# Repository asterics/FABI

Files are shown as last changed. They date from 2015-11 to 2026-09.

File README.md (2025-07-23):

# Welcome to FABI

The FABI (Flexible Assistive Button Interface) allows control of a computer’s mouse cursor or
keyboard by just using momentary switches. This can be helpful for people who want to create 
user interactions with the press of a button - and it allows people who can't use standard computer input devices
to play games, surf the internet, communicate and much more.

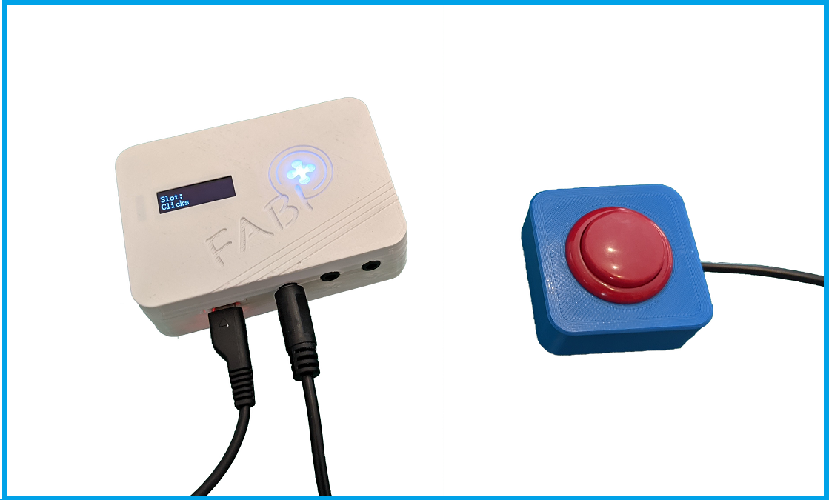
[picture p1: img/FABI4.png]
A FABI box with attached 3d-printed switch FABI box with attached switch


## How?

The FABI Interface can be actuated via dedicated buttons, momentary switches or self-made
electrical contacts. Additionally, a sip-puff sensor can be used to create user input.
FABI consists of a hardware module (a low-cost microcontroller which behaves
as a computer mouse and/or keyboard) and a config manager software for configuration of
the desired functions. The FABI system can be attached to computers, tablets or smart phones via USB.
Additionally, a bluetooth-module is available for devices that do not have a USB port (some Android or iOS phones).

## Folder structure of this repository
Essential information can be found in the following folders
* _Case Designs:_ different 3d-printable / lasercut designs for enclosures
* _Documentation:_ all user and construction manuals
* _img:_ some images of FABI variants
* _hardware:_ the KiCad design files and models for schematics and PCB layout
* _Settings:_ demo configurations which can be loaded into the FABI device via the GUI

The source of the current web based config manager can be found in another repository: [source of web based config manager](https://github.com/asterics/Addon-Bluetooth-WebGUI/tree/main/webgui)

## Configuration Manager and User manual

The FABI system does not ony offer fixed mappings of buttons to functions - it allows storing multiple configuration settings and changing them "on-the-fly". For configuration the [web-based config manager](https://fabi.asterics.eu/) should be used.
You can find information how to configure the individual button functions and system options in the user manual:

* [English user manual for configuration manager](https://github.com/asterics/FABI/blob/master/Documentation/UserManual/Markdown/Fabi%20User%20Manual.md) 
* [German user manual for configuration manager](https://github.com/asterics/FABI/blob/master/Documentation/UserManual/Markdown/Fabi%20Anwendungsanleitung.md)

## Building the hardware

There are various options for building FABI-compatible switch interfaces: you can order parts and build our construction kit, or make a completely self-driven version.
The most affordable version consists of just a microcontroller and attached momentary switches (material cost: a few bucks ...). The construction kit offers a PCB, LC-Display, 
Neopixel color led for indication of active configuration and optional modules (pressure sensor for sip/puff use, Bluetooth module for wireless access to phones/tablets etc.)
Following documentation is available for these different approaches:
* **Construction kit / PCB Version**: for building the FABI PCB Version from the construction kit.\
See [Construction kit building guide](https://github.com/asterics/FABI/blob/master/Documentation/ConstructionManual/PCB-Version/FABIManual.pdf)
* **DIY Building Guide - "intermediate"**: guide for creating a FABI device with a bare microcontroller and the provided 3d-printed enclosures.\
See [English version of construction manual](https://github.com/asterics/FABI/blob/master/Documentation/ConstructionManual/3D-printedBox/en/FABI_ConstructionManual.pdf) 
or [German version of construction manual](https://github.com/asterics/FABI/blob/master/Documentation/ConstructionManual/3D-printedBox/de/FABI_Bauanleitung.pdf)
* **DIY Building Guide - "all-selfmade"**: guide for creating a FABI device with a bare microcontroller and without the provided 3d-printed enclosures.\
See [DIY Building Guide](https://github.com/asterics/FABI/blob/master/Documentation/ConstructionManual/SelfmadeBox/FABI_Construction_SelfmadeBox.pdf)

## Building and Installing the Firmware

The FABI system consists of a firmware part which runs on a Raspberry Pi Pico microcontroller.
Since Version v3.7, the firmware development for the FABI (and our other alternative input devices) happens in a dedicated repository, see [FabiWare](https://github.com/asterics/FabiWare).
All firmware versions until v2.8 can be found in this repository by browsing the release section or by using the desired tags.
For information about the older firmware for the Arduino Pro Micro microcontroller, and the optional [Bluetooth Module](https://github.com/asterics/esp32_mouse_keyboard) which was used in the legacy hardware version, see https://github.com/asterics/FABI/wiki
Please __note__ the COM-Port installation instructions for older Windows systems (Win7/8) [here](https://github.com/raspberrypi/pico-feedback/issues/118).

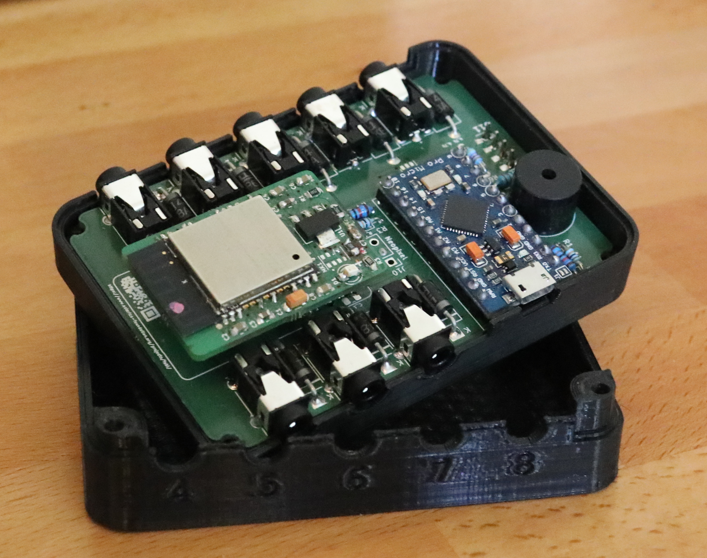
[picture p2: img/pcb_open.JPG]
FABI PCB version, equipped with Bluetooth Module FABI PCB version with equipped bluetooth module


## Example setups and applications

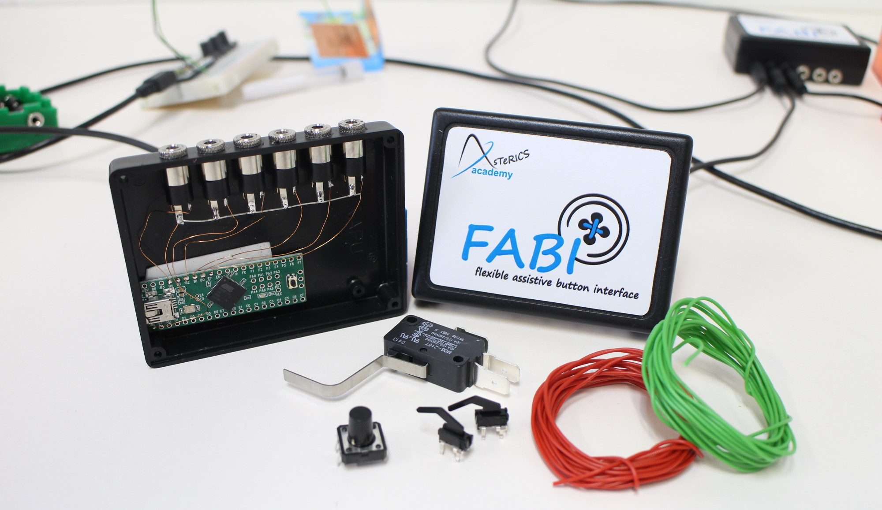
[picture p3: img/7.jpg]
An opened FABI box, where you can see the Teensy microcontroller board and the 6 jackplugs FABI box with jackplugs

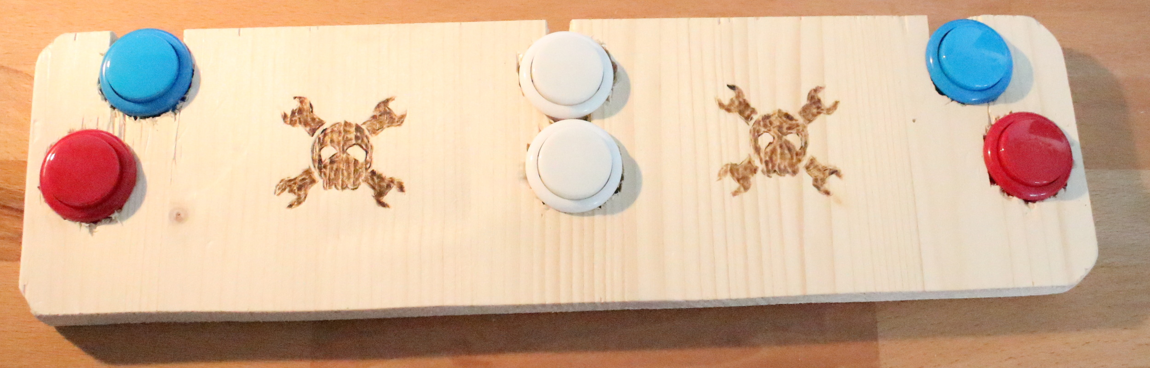
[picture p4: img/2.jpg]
A wooden piece with 6 buttons, arranged between, left and right of your hands. Enabling faster working with shortcuts on each button RapidCoding prototype, powered by FABI

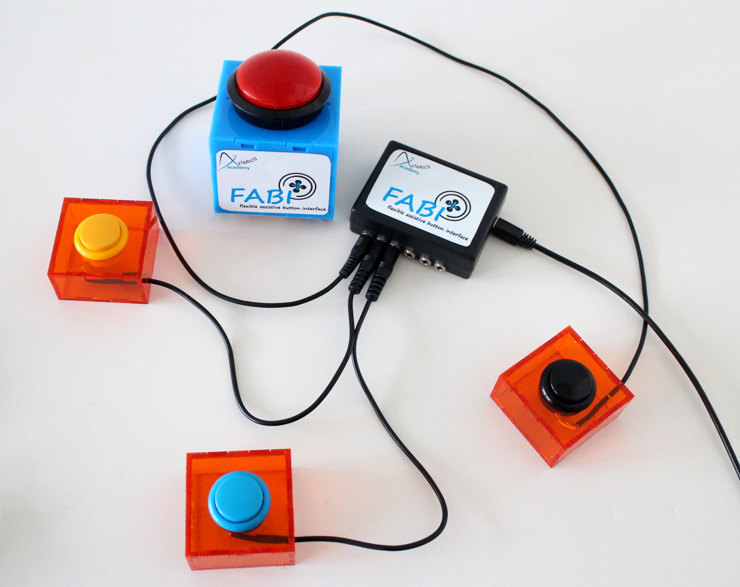
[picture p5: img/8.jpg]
A FABI box, where 3 different external buttons are connected FABI box with external buttons


# Links and Credits

Most of the work for FABI has been accomplished at the UAS Technikum Wien in course of the R&D-projects *ToRaDes* (MA23 project 18-04) and *WBT* (MA23 project 26-02), which have been supported by the [City of Vienna](https://www.wien.gv.at/kontakte/ma23/index.html),
see: [ToRaDes Project Information](https://embsys.technikum-wien.at/projects/torades/index.php), [Webpage WBT project](https://wbt.wien).

Have a look at the [AsTeRICS Foundation homepage](https://www.asterics-foundation.org) for applications and our other Open Source projects:

* [The FLipMouse controller](https://github.com/asterics/FLipMouse) - an open source alternative input device for controlling computers and mobile devices with minimal muscle movement.
* [The FLipPad controller](https://github.com/asterics/FLipMouse) - a flexible touchpad for controlling computers and mobile devices with minimal muscle movement.
* [Asterics Grid Open Source AAC](https://grid.asterics.eu) - an open source, cross plattform communicator / talker for Augmented and Alternative Communication (AAC).
* [The AsTeRICS framework](https://github.com/asterics/AsTeRICS) - provides high flexibility for building Assistive Technology solutions. 

# Support us
Please support the development of Open Source Assistive Technology projects by donating to the AsTeRICS Foundation:

<div>
<a title="Donate with PayPal" href="https://www.paypal.com/donate/?hosted_button_id=38AJJNS427MJ2" target="_blank" style="margin-right:3em">
</a>
<span>&nbsp;&nbsp;&nbsp;</span>
<a title="Donate at opencollective.com" href="https://opencollective.com/asterics-foundation" target="_blank">
</a>
</div>

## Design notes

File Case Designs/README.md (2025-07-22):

# FABI - case designs

This folder contains the design files for the 3D printed case for FABI3.

### Software

FreeCAD v1.1.0, x86_64 Linux

### Print file selection

These case files require a FABI v3.3, with battery and speaker support.

| FABI type                                           | Top                     | Bottom                         |
| --------------------------------------------------- | ----------------------- | ------------------------------ |
| Pico with 5mm socket, no pressure sensor/pipe       | FABI_Top_PicoSocket.stl | FABI_Bot_PicoSocket_NoPipe.stl |
| Pico with 5mm socket, hole for pressure sensor pipe | FABI_Top_PicoSocket.stl | FABI_Bot_PicoSocket_Pipe.stl   |
| Pico directly soldered, no pressure sensor/pipe     | FABI_Top.stl            | FABI_Bot.stl                   |

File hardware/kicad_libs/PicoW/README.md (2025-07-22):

## [**Download the latest release**](https://gitlab.com/recursivenomad/ki-lime-pi-pico/-/releases/)

**A comprehensive KiCad Library for the Raspberry Pi Pico** 🥧
====================================================================

### Providing footprints, symbols, and models for the module in its various forms and implementations

&nbsp;

***Features***
==============

- **KiCad 7.0 support**
- **Schematics with alternate pin definitions** to select more specific behaviours for each GPIO, as well as specify power directionality
- **Generic and specific footprints** for the Pico and Pico W
  - Through-hole and surface-mount footprints with and without mounting holes
  - Hand-solderable test points (ie. USB signals) in footprints with underside castellations
  - Optional pin labels as an add-on footprint
  - Optional keepout zone for 2.4 GHz RF on shared footprints
- **Diverse 3D models** for surface-mount, through-hole, and socketed forms of the Pico, Pico H, Pico W, and Pico WH using photorealistic materials
- Majority adherence to the [KiCad Library Conventions](https://klc.kicad.org/) version 3.0.34

&nbsp;

***How do I use this library?***
================================

- Ensure you are running KiCad 7.0 or later
- Download the most recent [release](https://gitlab.com/recursivenomad/ki-lime-pi-pico/-/releases/) of the library
- Unzip the file contents
- If not already created, create a new KiCad project
- Move the root library directory `RaspberryPi_Pico/` to a folder anywhere within your KiCad project
  > *If using the library globally, move `RaspberryPi_Pico/` to a globally accessible location*
- Open the relevant KiCad project
- Select `Preferences > Manage Footprint Libraries...`
- Select the `Project Specific Libraries` tab
  > *If using the library globally, select the `Global Librarires` tab instead*
- Click the folder icon in the lower left to `Add Existing`
- Navigate to and select `.../RaspberryPi_Pico/Module_RaspberryPi_Pico.pretty/`
- Click `OK`
- Select `Preferences > Manage Symbol Libraries...`
- Select the `Project Specific Libraries` tab
  > *If using the library globally, select the `Global Libaries` tab instead*
- Click the folder icon in the lower left to `Add existing library to table`
- Navigate to and select `.../RaspberryPi_Pico/MCU_Module_RaspberryPi_Pico.kicad_sym`
- Click `OK`

To use, simply add a symbol to your schematic as you would any other; symbols should be located under the section `MCU_Module_RaspberryPi_Pico`, and footprints under `Module_RaspberryPi_Pico`.

### **You're all set to design exciting new circuit boards using the Raspberry Pi Pico! 🎉**

&nbsp;

***Further reading***
=====================

## Other KiCad implementations of the Raspberry Pi Pico:

*Some adjacent solutions I encountered during my research for this project*

- Official Raspberry Pi KiCad library files for the Pico and Pico W provided in
  [Hardware design with the RP2040, Section 3](https://datasheets.raspberrypi.com/rp2040/hardware-design-with-rp2040.pdf#page=15)
    - https://datasheets.raspberrypi.com/rp2040/VGA-KiCAD.zip
    - https://datasheets.raspberrypi.com/rp2040/VGA-PicoW-KiCAD.zip
- A detailed SketchUp model of the surface-mount Pico incorporating the above
  Pico library
  - https://github.com/ncarandini/KiCad-RP-Pico
- A similarly versatile library found on the [KiCad forums](https://forum.kicad.info/t/are-there-pi-pico-library-files-available-for-kicad-6/35844/12)
  for all the Pico variants, including a castellated *add-on board* footprint
  - https://gitlab.com/mgyger/kicad-symbols/-/blob/pico/MCU_Module.kicad_sym
  - https://gitlab.com/mgyger/kicad-footprints/-/tree/pico/Module.pretty

## Pico W antenna radiation pattern resources:

- Great teardown featured:
  - https://electronupdate.blogspot.com/2022/07/raspberry-pi-pico-w-silicon-level.html
    - https://youtu.be/dWJE1ALMlBw
- Antenna info:
  - https://www.antenna-theory.com/design/raspberry-pi-antenna.php
    - https://youtu.be/MQ8gCsPoo6k
  - https://www.tablix.org/~avian/blog/archives/2022/03/effect_of_ground_cutout_on_the_cm4_antenna/
- Possible antenna radiation pattern:
  - https://abracon.com/parametric/antennas/PRO-EB-592
    - https://abracon.com/datasheets/PRO-EB-592.pdf
  - https://abracon.com/parametric/antennas/PRO-EB-594
    - https://abracon.com/datasheets/PRO-EB-594.pdf
  - https://embeddedcomputing.com/technology/analog-and-power/power-semiconductors-wireless-charging/a-lesson-in-wireless-engineering-from-the-raspberry-pi
  - https://antennatestlab.com/antenna-examples/raspberry-pi-model-3b-antenna-evaluation-gain-pattern

&nbsp;

***License***
=============

This work is licensed under the [*MIT No Attribution*](https://opensource.org/license/mit-0/)
license, the text of which should be found in [`LICENSE.txt`](./LICENSE.txt)
in the root directory of this project alongside this README.

*The license applies to all relevant files contained within the directory it*
*resides, including sub-directories, unless otherwise overridden by the*
*presence of another LICENSE file, or license header within a file.*

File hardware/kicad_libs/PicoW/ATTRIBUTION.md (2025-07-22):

# Ki-Lime Pi Pico project attributions

## Peter S. Hollander

Model, footprint, and symbol [source files and documentation](https://gitlab.com/recursivenomad/ki-lime-pi-pico)
created and compiled by Peter S. Hollander between 2022 and 2023, and made
freely available under the [*MIT No Attribution*](https://opensource.org/license/mit-0/) license.

## Melissa Lee

Source project title "Ki-Lime Pi" created by Melissa Lee in 2022, and donated
with unconditional permission 🥧

## Markus Gyger

Comprehensive alternate pin definitions as defined in the RP2040 datasheet
inspired by the [schematic symbol](https://gitlab.com/mgyger/kicad-symbols/-/blob/pico/MCU_Module.kicad_sym)
created by Markus Gyger.

## Raspberry Pi

Original assets which were referenced for geometry/organisation (model, symbol,
footprint) acquired from Raspberry Pi in 2022 via:

- [Raspberry Pi Pico Datasheet](https://datasheets.raspberrypi.com/pico/pico-datasheet.pdf)
  - Pico Model: <https://datasheets.raspberrypi.com/pico/Pico-R3-step.zip>
- [Raspberry Pi Pico W Datasheet](https://datasheets.raspberrypi.com/picow/pico-w-datasheet.pdf)
  - Pico W Model: <https://datasheets.raspberrypi.com/picow/PicoW-step.zip>
- [RP2040 Datasheet](https://datasheets.raspberrypi.com/rp2040/rp2040-datasheet.pdf)
- [Hardware design with the RP2040](https://datasheets.raspberrypi.com/rp2040/hardware-design-with-rp2040.pdf)
  - RP2040 Symbol: <https://datasheets.raspberrypi.com/rp2040/Minimal-KiCAD.zip>
  - Pico Footprint: <https://datasheets.raspberrypi.com/rp2040/VGA-KiCAD.zip>
  - Pico W Footprint: <https://datasheets.raspberrypi.com/rp2040/VGA-PicoW-KiCAD.zip>

&nbsp;

# Tools utilized

- [KiCad](https://www.kicad.org/) - Footprint/symbol library design
- [FreeCAD](https://www.freecad.org/) - Parametric 3D modelling
  - [KiCad StepUp addon](https://github.com/easyw/kicadStepUpMod) - VRML model exporting
- [VSCodium](https://vscodium.com/) - VRML model material bulk editing

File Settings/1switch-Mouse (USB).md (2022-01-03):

## Basic information
This configuration works with 1 switch (connected to input 1).
The switch controls the mouse pointer (press to move up/down/left/right).
Double-pressing the switch changes direction (activates the next slot).
A left click is performed automatically after 1 second of inactivity (dwell clicking).
(for double/right mouse clicks, a click selection tool (e.g. click2speak) can be used)
 
## Function assignment

### Slot1 (name: moveRight, color: blue, mode:USB)
- Button1 = move mouse right

### Slot2 (name: moveDown, color: orange, mode:USB)
- Button1 = move mouse right

### Slot3 (name: moveLeft, color: green, mode:USB)
- Button1 = move mouse right

### Slot4 (name: moveUp, color: red, mode:USB)
- Button1 = move mouse right

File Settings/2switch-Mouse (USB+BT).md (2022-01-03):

## Basic information
This configuration is optimised for 2 switches (connected to inputs 1 and 2)
It allows mouse pointer control on a PC/Mac/Laptop computer (USB-mode) 
and on a mobile device (iOS/Android, BT-mode).
 
Default mode is: USB
Button1 is used for moving the mouse in a given direction,
Button2 is used for changing the direction (short press) or the device mode (long press).
Left mouse clicks are performed automatically after a short period of inactivity (dwell clicking).
For double/right mouse clicks, a click selection tool (e.g. click2speak) can be used.

## Function assignment

### USB-Mode (slots 1-4, color: green):
- Button1 = move mouse cursor right/down/left/up
- Button2 = short-press: change mouse direction; long-press: switch to BT-Mode

### BT-Mode (slots 5-8, color: blue):
- Button1 = move mouse cursor right/down/left/up
- Button2 = short-press: change mouse direction; long-press: switch to USB-Mode

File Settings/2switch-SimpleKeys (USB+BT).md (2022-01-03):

## Basic information
This configuration works with 2 switches (connected to inputs 1 and 2).
Up to 8 switches might be used (for extended functions).
Button1 actuates the Space key, Button 2 actuates the Enter key.
The keys are sent to USB and Bluetooth (if a BT-device is paired).

The other buttons can be connected for actuating cursor keys and left/right mouse button.

## Function assignment

### Slot1 (name: keys-simple, color: purple, mode:USB+BT)
- Button1 = hold KEY_SPACE (space key)
- Button2 = hold KEY_ENTER (enter key)

optional:
- Button3 = hold KEY_UP (cursor up key)
- Button4 = hold KEY_DOWN (cursor down key)
- Button5 = hold KEY_LEFT (cursor left key)
- Button6 = hold KEY_RIGHT (cursor right key)
- Button7 = hold left mouse button
- Button8 = hold right mouse button

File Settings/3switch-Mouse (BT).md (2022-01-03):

## Basic information
This configuration is optimised for 3 buttons (connected to inputs 1, 2 and 3)
It allows mouse pointer control on a mobile device (e.g. Android) via bluetooth (BT-mode).
 
Button1 is used for moving the mouse pointer in the given direction.
Button2 is used for clicking the left mouse button.
A long press of Button2 creates a keyboards sequence for the Home-Key on many Android devices (GUI+Backspace).
Button3 is used for performing a swipe action in the given direction.
Changing the direction can be done be double-pressing any button.

## Function assignment

### Mouse control, BT Mode (slots 1-4, color: red,blue,turquoise,yellow):
- Button1 = move mouse cursor right/down/left/up
- Button2 = short-press: click left mouse button mouse direction; long press: Home-Key
- Button3 = swipe gesture right/down/left/up

double press any button: change direction

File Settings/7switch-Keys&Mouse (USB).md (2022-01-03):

## Basic information
This configuration is optimised for 7 buttons (connected to inputs 1-7).
It allows key control (for gaming) and mouse pointer control via USB.
Button 7 changes between key and mouse control.

## Function assignment

### cursorkeys (slot1, color: blue):
- Button1 = hold cursor up key (KEY_UP)
- Button2 = hold cursor down key (KEY_DOWN)
- Button3 = hold cursor left key (KEY_LEFT)
- Button4 = hold cursor right key (KEY_RIGHT)
- Button5 = hold space key (KEY_SPACE)
- Button6 = hold enter key (KEY_ENTER)
- Button7 = load next slot

### mouse (slot2, color: purple):
- Button1 = move mouse up
- Button2 = move mouse down
- Button3 = move mouse left
- Button4 = move mouse right
- Button5 = hold left mouse button
- Button6 = hold right mouse button
- Button7 = load next slot

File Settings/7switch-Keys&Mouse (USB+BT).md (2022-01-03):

## Basic information
This configuration is optimised for 7 buttons (connected to inputs 1-7).
It allows key control (for gaming), mouse pointer control via USB and mouse pointer control via Bluetooth (BT-mode).
Button 7 changes between these three modes.

## Function assignment

### cursorkeys (slot1, color: blue):
- Button1 = hold cursor up key (KEY_UP)
- Button2 = hold cursor down key (KEY_DOWN)
- Button3 = hold cursor left key (KEY_LEFT)
- Button4 = hold cursor right key (KEY_RIGHT)
- Button5 = hold space key (KEY_SPACE)
- Button6 = hold enter key (KEY_ENTER)
- Button7 = load next slot

### mouse (slot2, color: purple):
- Button1 = move mouse up
- Button2 = move mouse down
- Button3 = move mouse left
- Button4 = move mouse right
- Button5 = hold left mouse button
- Button6 = hold right mouse button
- Button7 = load next slot

### mouse-bt (slot3, color: yellow, BT):
- Button1 = move mouse up
- Button2 = move mouse down
- Button3 = move mouse left
- Button4 = move mouse right
- Button5 = hold left mouse button
- Button6 = hold right mouse button
- Button7 = load next slot

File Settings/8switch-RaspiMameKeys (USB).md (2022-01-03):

## Basic information
This configuration is dedicated for controlling the MAME game emulation software via USB keyboard/mouse (running e.g. on a RaspiberryPi computer).
You will need 8 buttons (connected to inputs 1-8) to access the essential functions for UI/menu and game control.
For more information about the MAME key mapping, see: [MAME default keys](https://docs.mamedev.org/usingmame/defaultkeys.html)

The first FABI slot provides standard mouse pointer control via USB, and the Escape key on button 7.
Slot 2 and 3 provide keyboard keys for menu and game navigation.
Button 8 changes between the three slots.

## Function assignment

### mouse (slot1, color: yellow):
- Button1 = move mouse left
- Button2 = move mouse up
- Button3 = move mouse right
- Button4 = move mouse down
- Button5 = click left mouse button
- Button6 = click right mouse button
- Button7 = hold escape key (KEY_ESCAPE)
- Button8 = load next slot

### mame1 (slot2, color: red):
- Button1 = hold cursor up key (KEY_LEFT)
- Button2 = hold cursor down key (KEY_UP)
- Button3 = hold cursor left key (KEY_RIGHT)
- Button4 = hold cursor right key (KEY_DOWN)
- Button5 = hold ALT key (KEY_ALT)
- Button6 = hold control key (KEY_CTRL)
- Button7 = hold 1 key (KEY_1)
- Button8 = load next slot

### mame2 (slot3, color: green):
- Button1 = hold cursor up key (KEY_LEFT)
- Button2 = hold cursor down key (KEY_UP)
- Button3 = hold cursor left key (KEY_RIGHT)
- Button4 = hold cursor right key (KEY_DOWN)
- Button5 = hold A key (KEY_A)
- Button6 = hold F1 key (KEY_F1)
- Button7 = hold enter key (KEY_ENTER)
- Button8 = load next slot

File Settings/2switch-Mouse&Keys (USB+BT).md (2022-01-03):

## Basic information
This configuration is optimised for 2 switches (connected to switch inputs 1 and 2), up to 6 switches might be used.
It allows mouse cursor control of a PC/Mac/Laptop computer (USB-mode) 
and switch access via Bluetooth on iOS/Android (BT-mode).
 
Default mode is: USB
Button1 is used for the primary function,
holding Button2 for > 1 second changes the mode.

## Function assignment

### USB-Mode (slots 1-4, color: green):
- Button1 = move mouse cursor right/down/left/up
- Button2 = short-press: change mouse direction; long-press: switch to BT-Mode
- Button3 = hold left mouse button
- Button4 = hold right mouse button
- Button5 = mouse wheel up
- Button6 = mouse wheel down

Buttons 3-6 are optional.
A left click is performed automatically after 2 seconds of inactivity (dwell clicking).
(for double/right mouse clicks, a click selection tool (e.g. click2speak) can be used)

### BT-Mode (slot 5, color: blue):
- Button1 = hold SPACE key
- Button2 = short-press: hold ENTER key; long-press: switch to USB-Mode
- Button3 = hold CURSOR-UP key
- Button4 = hold CURSOR-DOWN key
- Button5 = hold CURSOR-LEFT key
- Button6 = hold CURSOR-RIGHT key

Buttons 3-6 are optional.

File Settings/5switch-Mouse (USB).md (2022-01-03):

## Basic information
This configuration is optimised for 5 buttons (connected to inputs 1-5), up to 8 buttons might be used.
It allows mouse pointer control via USB.

## Function assignment

### Mouse (slot1, color: blue):
- Button1 = move mouse pointer up
- Button2 = move mouse pointer down
- Button3 = move mouse pointer left
- Button4 = move mouse pointer right
- Button5 = hold left mouse button
- Button6 = hold right mouse button
- Button7 = scroll mouse wheel up
- Button8 = scroll mouse wheel down

Buttons 6-8 are optional.
In order to perform right or double clicks, a click selection tool (e.g. click2speak) might be used.

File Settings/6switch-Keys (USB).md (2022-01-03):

## Basic information
This configuration is optimised for 6 buttons (connected to inputs 1-6), up to 8 buttons might be used.
It allows cursor key + space/enter key input (e.g. for gaming) via USB.

## Function assignment

### Cursorkeys (slot1, color: blue):
- Button1 = hold cursor up key (KEY_UP)
- Button2 = hold cursor down key (KEY_DOWN)
- Button3 = hold cursor left key (KEY_LEFT)
- Button4 = hold cursor right key (KEY_RIGHT)
- Button5 = hold space key (KEY_SPACE)
- Button6 = hold enter key (KEY_ENTER)

- Button7 = hold left mouse button
- Button8 = hold right mouse button
- Sip = scroll mouse wheel up
- Puff = scroll mouse wheel down

Buttons 7-8 and sip/puff functions are optional.

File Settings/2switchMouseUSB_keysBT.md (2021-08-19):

## Basic information
This configuration is optimised for 2 switches (connected to switch inputs 1 and 2)
It allows mouse cursor control of a PC/Mac/Laptop computer (USB-mode) 
and switch access via Bluetooth on iOS/Android (BT-mode).
 
Default mode is: USB
Button1 is used for the primary function, holding Button2 for > 2 seconds changes the mode.
(Buttons 3-6 are optional.)

## Function assignment

### USB-Mode (uses configuration slots 1-4):
- Button1 = move mouse cursor up/down/left/right
- Button2 = short-press: change mouse direction; long-press: switch to BT-Mode
- Button3 = hold left mouse button
- Button4 = hold right mouse button
- Button5 = mouse wheel up
- Button6 = mouse wheel down

### BT-Mode (slot 5):
- Button1 = hold SPACE key
- Button2 = short-press: hold ENTER key; long-press: switch to USB-Mode
- Button3 = hold CURSOR-UP key
- Button4 = hold CURSOR-DOWN key
- Button5 = hold CURSOR-LEFT key
- Button6 = hold CURSOR-RIGHT key

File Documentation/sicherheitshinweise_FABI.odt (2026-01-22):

Sicherheitshinweise & bestimmungsgemäße Verwendung

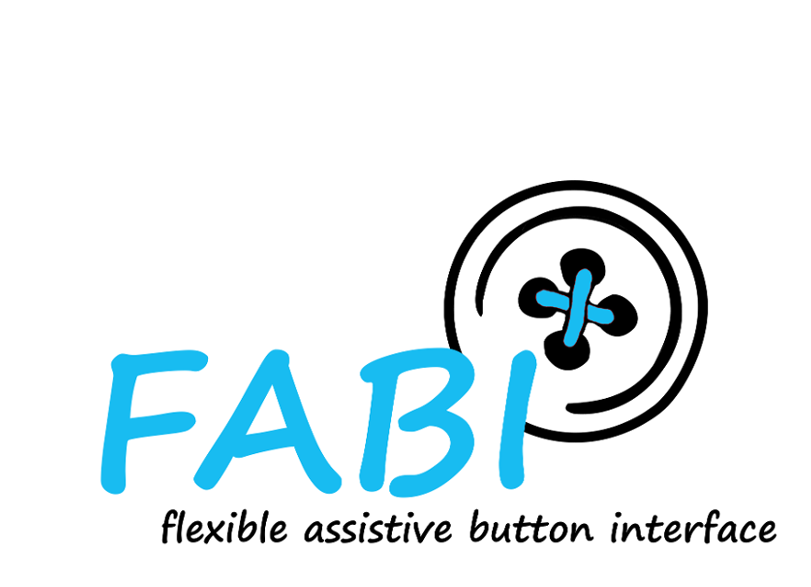
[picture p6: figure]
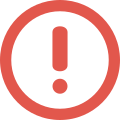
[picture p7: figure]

Lesen Sie diese Anweisungen sorgfältig vor der Verwendung des FABI. Abweichende Verwendung oder Missachtung dieser Anweisungen kann zu Schäden führen, für diese Schäden kann die AsTeRICS Foundation nicht haftbar gemacht werden!

- Das Gerät darf in keinem Fall in Kombination mit Medizingeräten oder sicherheitsrelevanten Geräten verwendet werden!
- Das FABI darf ausschließlich mit Unterhaltungselektronik verwendet werden.
- Die angeschlossenen Taster müssen dem entsprechenden Verwendungszweck angepasst sein. Im Zweifelsfall sollte eine fachkundige Person zu Rate gezogen werden.
- Verwenden Sie das Gerät nicht in explosiven Umgebungen (Sauerstoff)

FABI – DE Sicherheitshinweise v1.1 – office@asterics-foundation.org

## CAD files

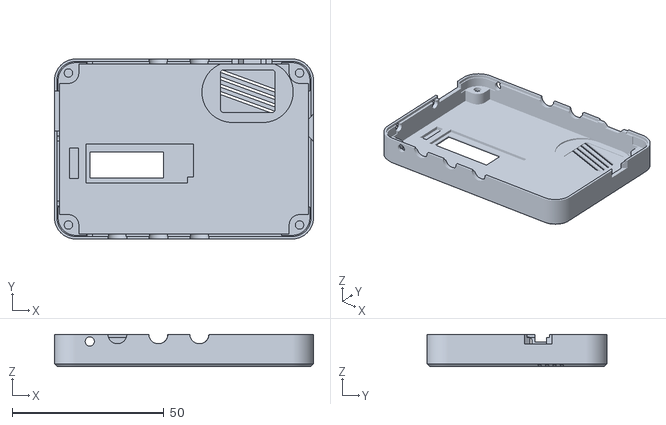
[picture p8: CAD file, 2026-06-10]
Case Designs/FABI_Top.stl
85.2 x 59.2 x 10.5

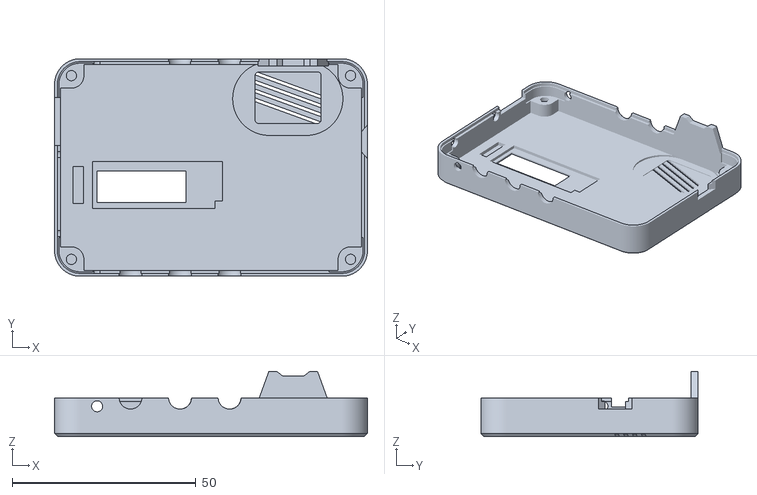
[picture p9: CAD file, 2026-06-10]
Case Designs/FABI_Top_PicoSocket.stl
85.2 x 59.2 x 17.8

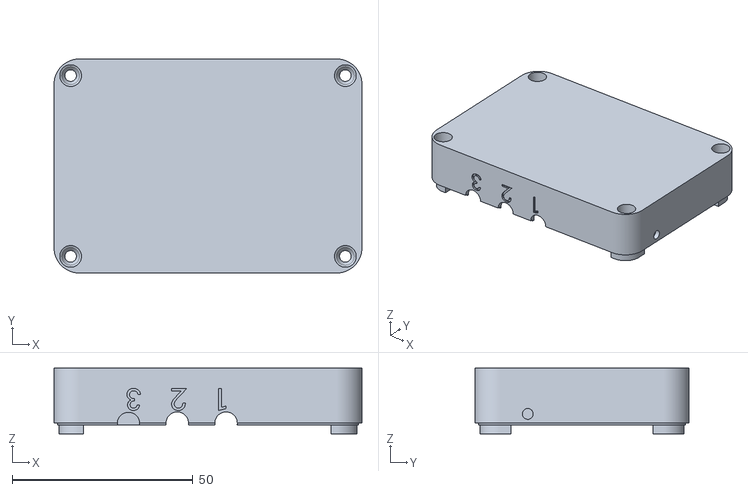
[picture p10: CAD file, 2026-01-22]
Case Designs/FABI_Bot_PicoSocket_NoPipe.stl
85.2 x 59.2 x 18.2

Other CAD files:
Case Designs/FABIv3.FCStd
Case Designs/FABI_Bot_PicoSocket_Pipe.stl
Case Designs/FABI_Bot.stl

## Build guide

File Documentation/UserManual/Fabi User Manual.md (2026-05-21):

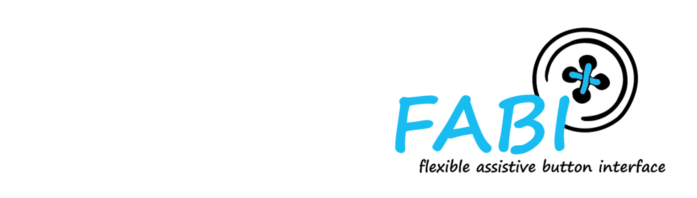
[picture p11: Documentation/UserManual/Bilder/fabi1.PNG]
FabiLogo


# FABI - User Manual

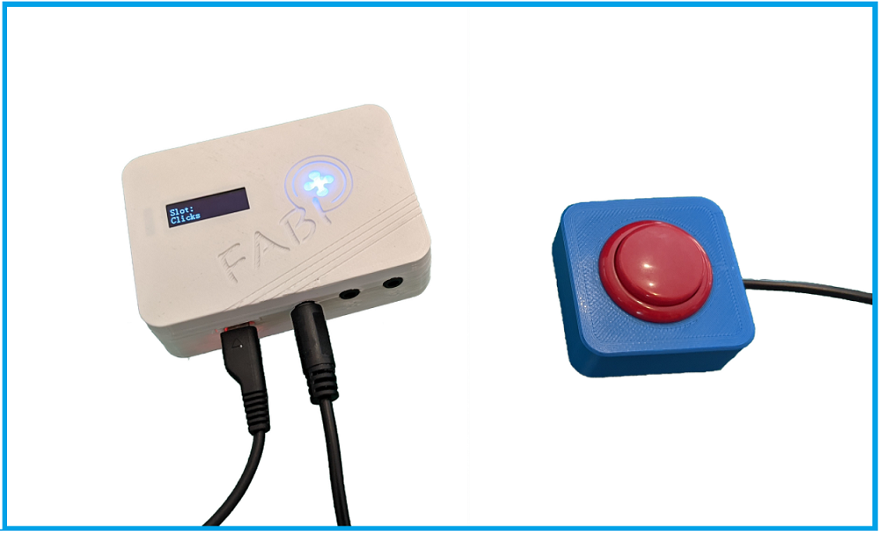
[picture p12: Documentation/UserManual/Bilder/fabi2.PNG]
FabiFoto


____

# Welcome to FABI

FABI - the "Flexible Assistive Button Interface" - connects up to five momentary switches (buttons) to a Personal Computer, smartphone or tablet, in order to perform complex mouse-, keyboard- and joystick actions. A configured FABI module can be used with any PC or mobile device (running Windows, Linux, macOS, iOS or Android) without installing additional software, because the FABI module behaves like an ordinary computer mouse/keyboard/joystick. Using FABI, people with limited motor capabilities can play computer games, surf the internet, write e-mails and much more.

[TOC]

## Introduction

The FABI system can be used with commercially available switches, inexpensive arcade buttons, or even homemade electrical contacts. FABI consists of a hardware module (an inexpensive microcontroller that acts as a computer peripheral), and optional add-on modules and sensors (sip/puff pressure sensor). A web-based graphical configuration editor (the *FABI configuration manager*) is available for setting up desired actions. 

Various actions are possible for each button, allowing different configurations to be stored in up to 10 memory slots (*configuration slots*). The configuration slots can be changed during operation, e.g. via a specific button, making FABI a very flexible alternative input system which allows control of even multiple devices (e.g. connected via USB and BT) via only a few buttons! 

FABI is available as an [open source construction kit](https://github.com/asterics/FABI)  including corresponding assembly instructions for the hardware. The first FABI version was developed in course of the *AsTeRICS Academy* project at the UAS (University of Applied Sciences) Technikum Wien. In 2017, the non-profit organization *AsTeRICS Foundation* was founded in order to foster open source assistive technology solutions and to make them available at low cost: [www.asterics-foundation.org](https://www.asterics-foundation.org/1270-2/).

All software modules, hardware design files, and "how-to"-documents are available under free and open source licenses and can be used and modified without fees. We have made every effort to select low-cost components without compromising functionality and flexibility - making FABI an affordable switch interface with extensive capabilities!

The **FABI configuration manager** enables to assign functions (actions) to connected switches (buttons). Once a configuration has been applied, it remains active, also if the power supply is removed. The FABI system can then be used to control different devices (e.g. Windows/Linux PCs, or Mac computers via USB connection or tablets / smart phones via USB-OTG or Bluetooth connection). The configuration manager is only needed if settings should be changed.

The configuration manager has to be opened in the *Chrome web browser* running on a PC or Mac. It can be found at the following web address: [https://fabi.asterics.eu](https://fabi.asterics.eu/index_fabi.htm). Figure 1 shows the Welcome page of the configuration manager. 

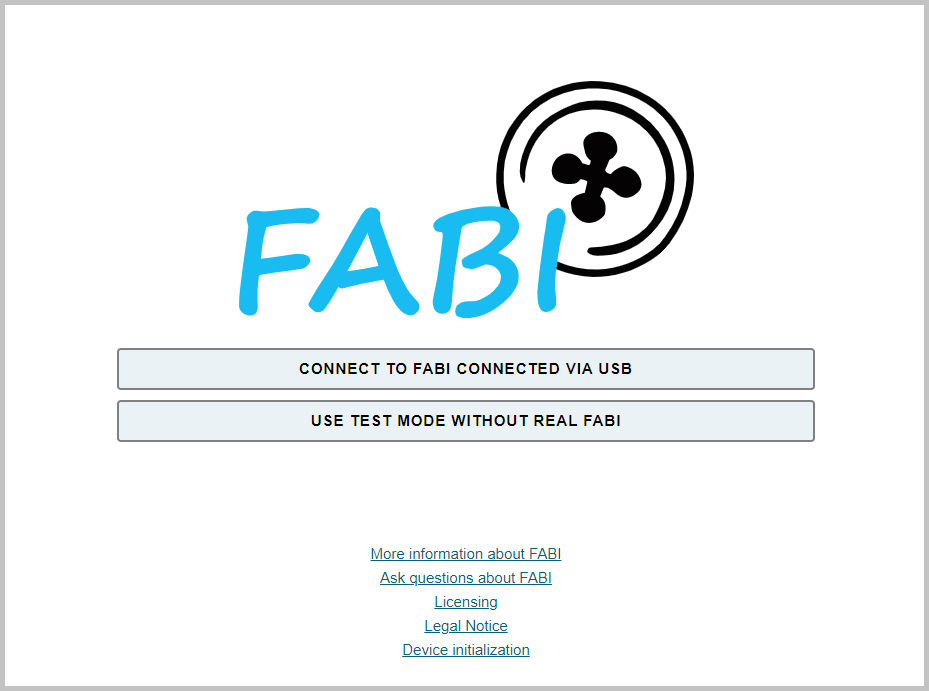
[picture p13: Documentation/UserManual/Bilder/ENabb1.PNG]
Abbildung1


*Figure 1*: Welcome page of the configuration manager

#### Connecting the FABI device

After the Welcome page of the configuration manager is visible, connect your FABI device to a USB port and perform the following steps: 

Abbildung2

*Figure 2*: Connecting the USB micro cable

1. Make sure that the FABI device is connected to the PC via a USB port, using a USB micro cable (see figure 2 above).
2. Click **CONNECT TO FABI CONNECTED VIA USB** on the configuration manager welcome page. ***Note*** that you could also have a look at the configuration manager's functions without connecting the FABI hardware, by using the Test Mode (which simulates a hardware connection).
3. A communication port identifier with a certain name (e.g. COM4 or /dev/ttyUSB1) should be displayed in a pop-up window. Click on this identifier and then click **Connect**. 
4. If you cannot see the user interface of the FABI configuration manager as in Figure 3, open the website again and reselect the communication port in the selection box. Then click **Connect**.

## Using the configuration manager

After connecting to the communication port of the FABI system, you will see the user interface of the FABI Configuration Manager, with the *ACTIONS Tab* opened (Figure 3). 

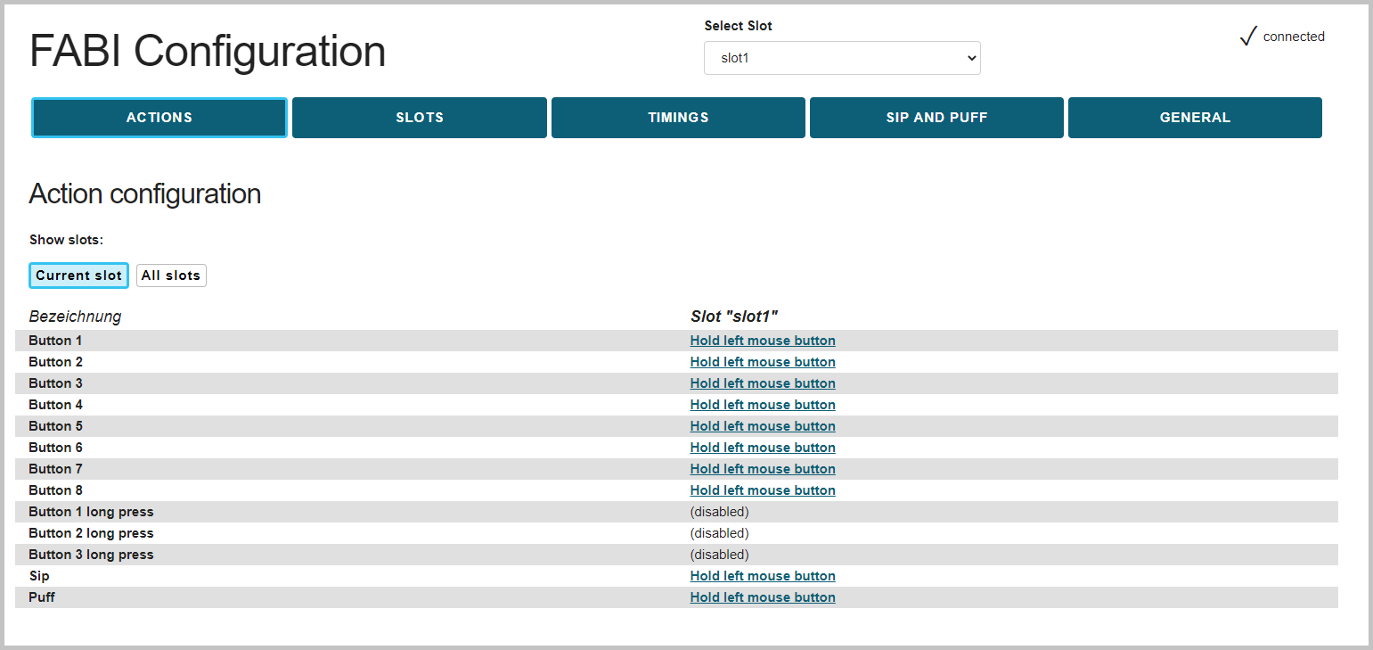
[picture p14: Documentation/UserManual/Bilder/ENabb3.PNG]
Abbildung3
 

*Figure 3*: FABI Configuration Manager User Interface, *ACTIONS Tab* opened

#### Port Status

The port status is displayed at the top right corner, it shows whether the FABI device is currently connected to the configuration manager. If the device is disconnected, the Welcome page will automatically be displayed again.

#### Save settings

Any changes in the settings are automatically applied and saved in the FABI device. The configurations are retained even if the FABI system is disconnected from the USB cable or power supply.

## *ACTIONS Tab*: Assigning Button Functions

In the *ACTIONS Tab*, different functions (actions) can be assigned to (up to) 8 buttons. Possible actions include various mouse clicks, mouse movements, operation of the mouse scroll wheel or keyboard keys. You can change the action for a desired button by clicking the underlined (currently active) action next to the button name - see red square in Figure 4.1. Then, a pop-up window appears where the desired action category and the desired action can be selected. ***Note:*** If more than 8 buttons are needed, several FABI modules can be operated in parallel.

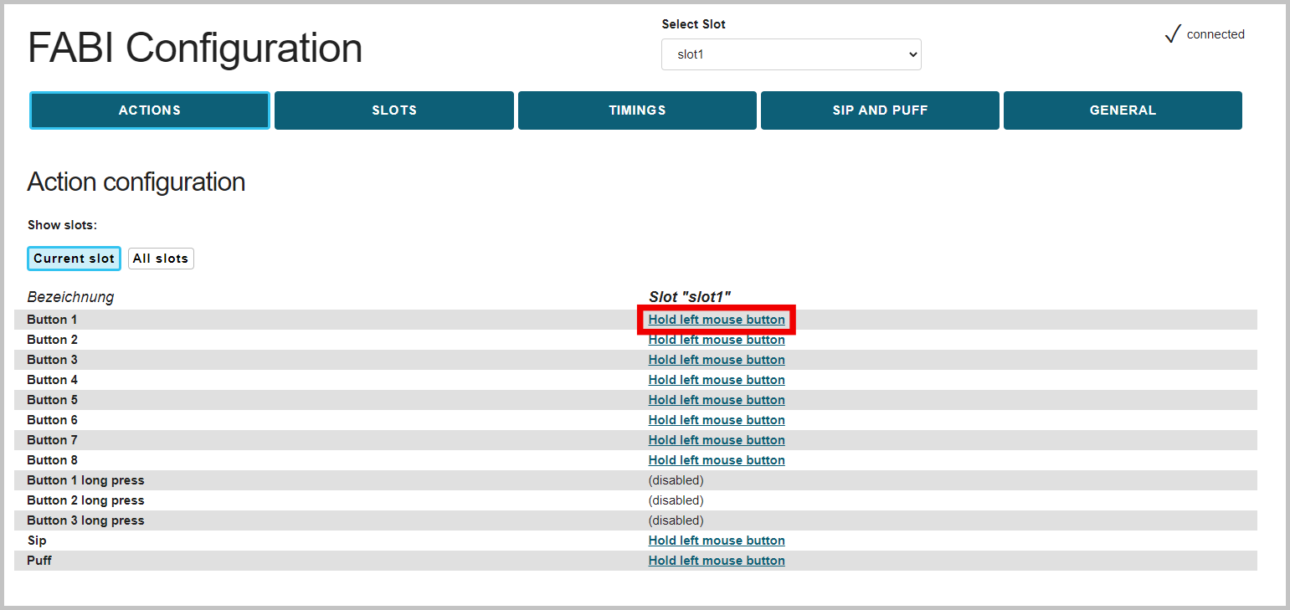
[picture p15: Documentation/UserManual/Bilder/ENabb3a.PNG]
Abbildung4.1
 

*Figure 4.1*: Select/change action for button

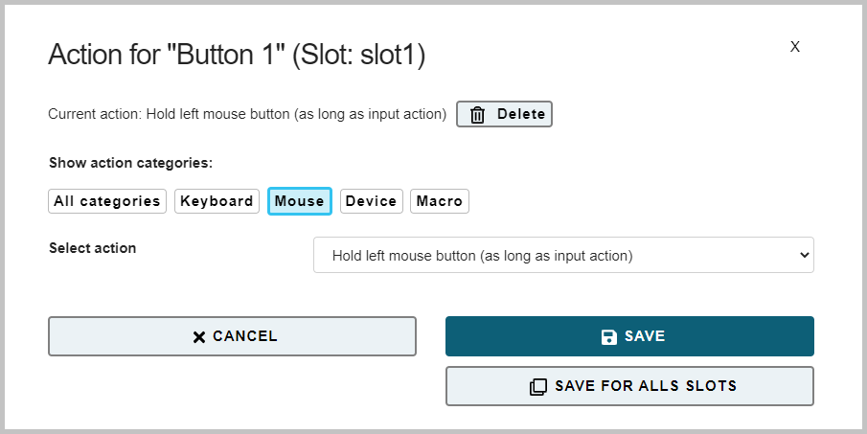
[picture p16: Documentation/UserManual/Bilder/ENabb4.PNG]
Abbildung4.2
 

*Figure 4.2*: Select action for a button (here: button 1)

***Note:*** The action settings are applied to the active configuration slot by clicking **SAVE**, but can also be applied to all slots by clicking **Save for all slots** (see chapter *Using configuration slots*).

### Action category: Mouse

In the following, the actions of category *Mouse* are briefly explained:

#### Hold Left/Right/Middle Mouse Button (as long as input action)

These actions allow to press (and hold) the left, right or middle mouse button. The mouse button remains pressed as long as the button is held (for example, for dragging files or folders it is necessary to keep the left mouse button pressed).

#### Click left/right/middle mouse button

With these actions, a single click of the left, right or middle mouse button can be executed by pressing the button. ***Note*** that a click consists of pressing & releasing the corresponding mouse button with a short delay, no matter how long the button is held!

#### Double-click left mouse button

By assigning this action, a double click of the left mouse button can be performed by a single press of the assigned button. (Double-clicking the left mouse button is necessary e.g. in order to to open a file - however, performing quick mouse clicks can be difficult for some users.) 

#### Press or release left/right/middle mouse button (toggle).

These actions change the state of the left, right or middle mouse button when the assigned button is pressed. ***Note*** that the mouse button remains pressed until the button is pressed again!

#### Scroll down / scroll up

The actions "Scroll up" and "Scroll down" create activities with the scroll wheel of the computer mouse. Pressing the button will cause one scroll action (upwards or downwards respectively), with a selectable step size. (Useful for reading documents or web pages).

#### Move mouse horizontally / vertically - mouse movement in x or y direction.

The "Move mouse horizontally (x-axis)" and "Move mouse vertically (y-axis)" actions generate computer mouse movements along the selected axes. Speed parameters can be set in the field that appears below. When the button is pressed, the mouse pointer is accelerated up to this maximum speed (e.g. 20 or -20, see figure 5).

*A positive value for the X direction moves the mouse pointer to the right.
A negative value for the X-direction moves the mouse pointer to the left.
A positive value for the Y direction moves the mouse pointer down.
A negative value for the Y direction moves the mouse pointer upward.*

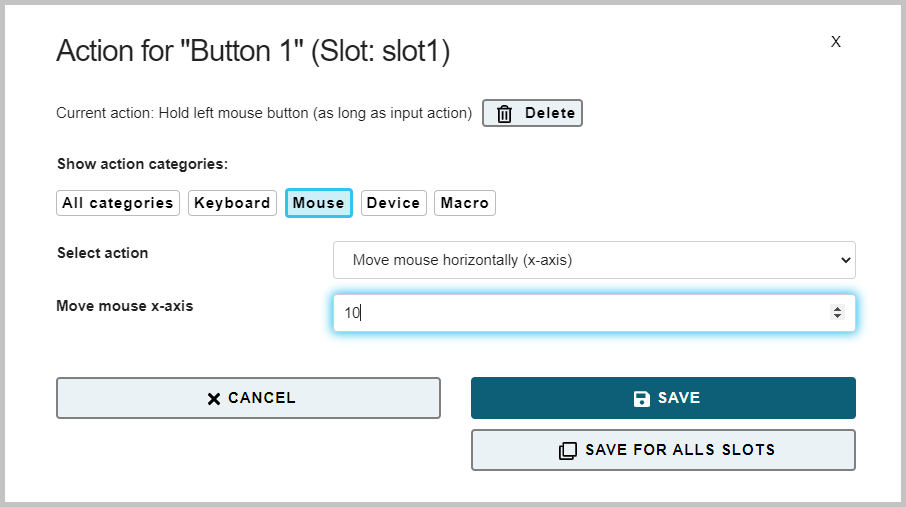
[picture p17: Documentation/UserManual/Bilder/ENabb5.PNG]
Abbildung5
 

*Figure 5*: Screenshot of the "Move mouse horizontally (x-axis)" action and speed setting.

### Action category: Keyboard

In the following, the actions of category *Keyboard* are briefly explained:

#### Hold key(s) (as long as input action)

This action presses (and holds) desired keys (or key combinations) as long as the corresponding button is pressed. The desired keyboard key(s) can be selected from a dropdown selection box or recorded directly from the keyboard input (see key selection explaination below, figure 6).

#### Press key(s) + release automatically

This action pressed desired keys (or key combinations). The keyboard keys are pressed and released immediately (i.e. not held down as long as the button is pressed). The desired keyboard key(s) can be selected from a dropdown selection box or recorded directly from the keyboard input (see key selection explaination below, figure 6).

#### Press or release key(s) (toggle)

This action allows desired keys (or key combinations) to change their state (i.e. pressed or released) every time the button is pressed. ***Note*** that the keyboard key remains pressed until the button is pressed *again*! 

**Key selection explained:**
The desired keyboard key can be chosen from a selection box (left of the "Add" button). After clicking **ADD**, the selected key name (key identifier) appears in "Insert Keys" field, indicating that this key is now assigned to the button. Multiple keys can be added for generating key combinations / keyboard shortcuts. 
Figure 8 shows how to assign keyboard key "KEY_D" to button 1. This will cause a lowercase "d" to be written each time button 1 is pressed. 
Alternatively to the selection box, keys or key combinations can also be recorded from live keyboard input by clicking the "Insert keys" field (left of the "Clear" button). 
Keys that have already been assigned can be removed by clicking **CLEAR**.

***Note:*** With "KEY_SHIFT" in combination with letter keys, capital letters can be created. All supported key names (identifiers) can be found in the [appendix](https://github.com/asterics/FABI/blob/master/Documentation/UserManual/Markdown/Fabi%20User%20Manual.md#supported-key-identifiers).

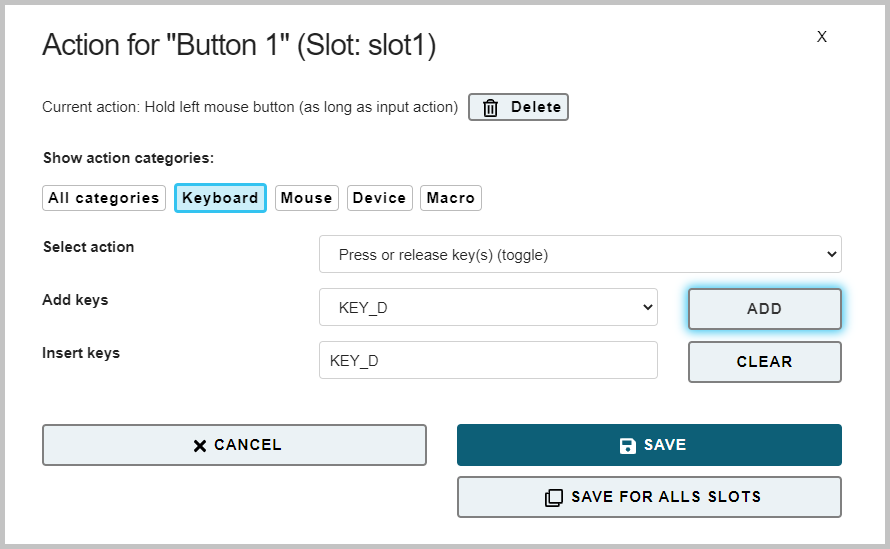
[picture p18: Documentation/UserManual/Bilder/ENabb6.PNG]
Abbildung6
 

*Figure 6*: Key selection (here for the "Press or release key(s) toggle" action)

#### Write word

The "Write word" action allows to write a certain text every time the button is pressed. This can be useful for entering passwords, command strings etc. When you select "Write word", an empty text field appears under the drop-down selection box, where the desired text can be entered:

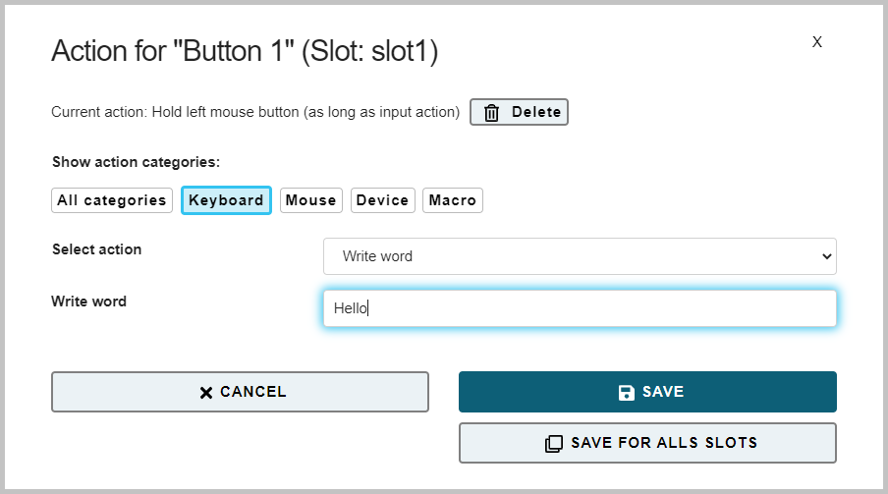
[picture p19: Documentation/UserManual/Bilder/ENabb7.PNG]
Abbildung7
 

*Figure 7*: Screenshot of the "Write word" action

### Action category: Joystick

In the following, the actions of category *Joystick* are briefly explained:

**Joystick set x-/y-/z-axis/slider**
These actions can be used to send a desired value to the joystick axis. The selectable joystick axes are: *X / Y / Z / Z-Turn / slider*. The joystick is moved back to middle position when the associated user activity ends.

**Press Joystick Button**
This action can be used to press a desired joystick button. The FLipMouse device supports 32 buttons, so any value from 1 to 32 is allowed. The joystick button is released when the associated user activity ends.

**Joystick hat position**
This action sets the orientation of the joystick "hat" (in degrees). Allowed values are:
*-1, 0, 45, 90, 135, 180, 225, 270, 315*. The value of -1 sets the hat to the middle (idle) position. 
The joystick hat is moved back to middle position when the associated user activity ends. 

### Action category: Infrared

**Play / Hold / Stop Infrared Command**
This action replays the infrared (IR-)code with the given command name. The existing (recorded) IR-commands can be selected from the drop-down menu. The *play* action sends the recorded code once, whereas the *hold* action repeats the code until the user activity ends. 

<p align="left" width="100%">
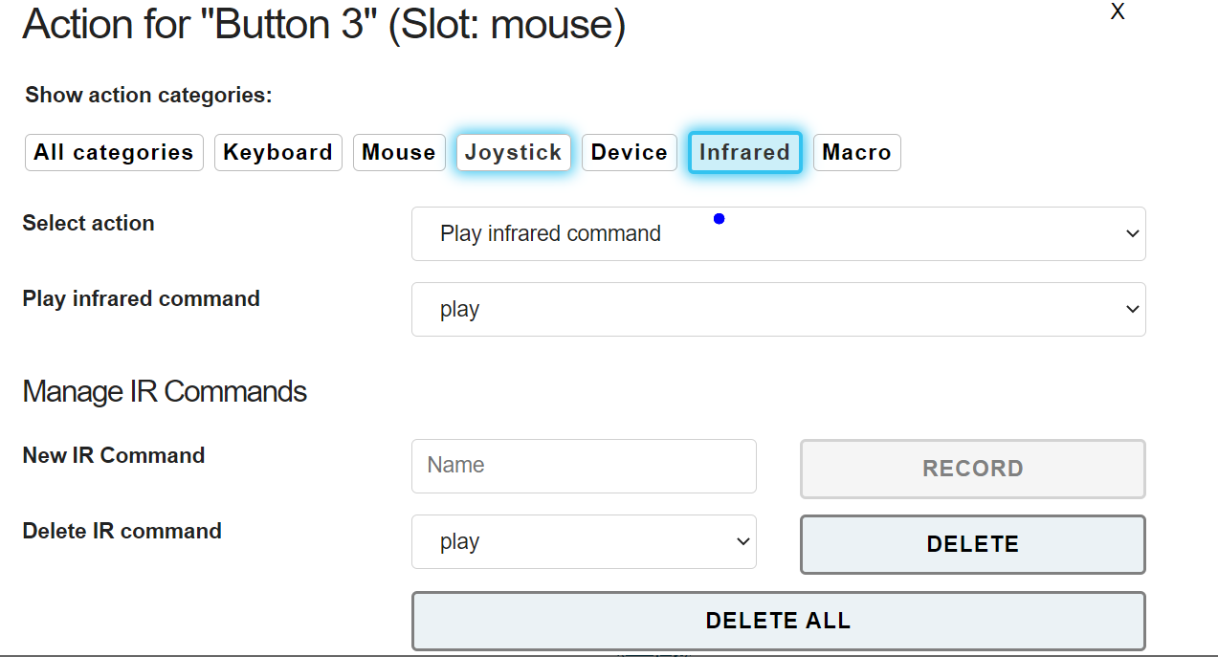
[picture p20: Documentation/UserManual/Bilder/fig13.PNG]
    
</p>
*Figure 8: Infrared Recording and Replay Configuration Manager*

The FABI device includes an infrared remote control receiver module and four high current IR LED so that it can record and replay remote control codes of many remote control devices used in consumer electronics. If you want to use this feature of the FABI, make sure that the IR sending LED is points towards the device you want to control.

To record a new IR code, go to the tab ACTIONS. Click the desired action and select the action category “**Infrared**” in the popup-window. There, three different types of IR-actions can be selected from the combo box:

* *Play infrared command*: sends the recorded code once
* *Hold infrared command*: repeats the code until the user activity ends
* *Stop infrared command*: stops a currently plaing IR-code

The existing commands can be chosen from the drop-down menu.

In this window you can also manage IR commands. Next to *New IR Command*, you can enter a name and then click RECORD - point your IR remote to the side of the FABI where it is marked as __IR__ and send the IR command (there is a 10 seconds time limit for the recording phase). The new command is now stored in the FABI and can be chosen and replayed by selecting it's name in the drop down menu. If the command is not correctly replayed, try to increase the IR-Code timeout – for example to 250 milliseconds. Using *Delete IR command* commands can be deleted. 

### Action category: Device

In the following, the actions of category *Device* are briefly explained:

#### No command (empty)

If *No command (empty)* is selected, the corresponding button will be disabled.

#### Load next slot - switch to next configuration

As soon as the button is pressed, the next configuration slot is activated. This allows the individual slots to be changed sequentially, using the assigned button. After the last configuration, the first configuration is automatically activated. (This action is only relevant if you stored configurations into multiple memory slots - for an explaination of the slot system please refer to chapter "Using configuration slots").

#### Load slot by name - switch to configuration with specific name

As soon as the button is pressed, the configuration with the specified name is activated. (This action is only relevant if you stored configurations into multiple memory slots - for an explaination of the slot system please refer to chapter "Using configuration slots" below).

### Action category: Macro

#### Custom Macro - Execute Macro Commands

This advanced feature allows multiple commands to be executed using appropriate command shortcuts, providing a high degree of flexibility. The individual commands are entered in the text field, separated by semicolons. Command shortcuts can also be selected using "Add Command" and then be added to the macro using "ADD". If several commands are added in succession, the semicolons are entered automatically.
Example: The macro command `MX 10; WA 500; KP KEY_A;` moves the mouse cursor 10 pixels to the right, then waits 500 milliseconds and presses the keyboard key "A".
***Note:*** Supported commands are listed in the combobox "Add command". However, commands and keyboard shortcuts can also be entered manually into the "Macro" field. A complete list of supported commands can be found in the [appendix](https://github.com/asterics/FABI/blob/master/Documentation/UserManual/Markdown/Fabi%20User%20Manual.md#supported-macro-commands).

## *SLOTS Tab*: Using Configuration Slots

Various action assignments for the buttons can be stored in up to 10 memory locations (*configuration slots*). The active configuration slot can also be changed during operation, e.g. via a specific button (see actions). As soon as the FABI device is supplied with power via the USB cable, the first configuration slot is automatically activated. The slots can be created and managed by opening the *SLOTS Tab*, see Figure 9:

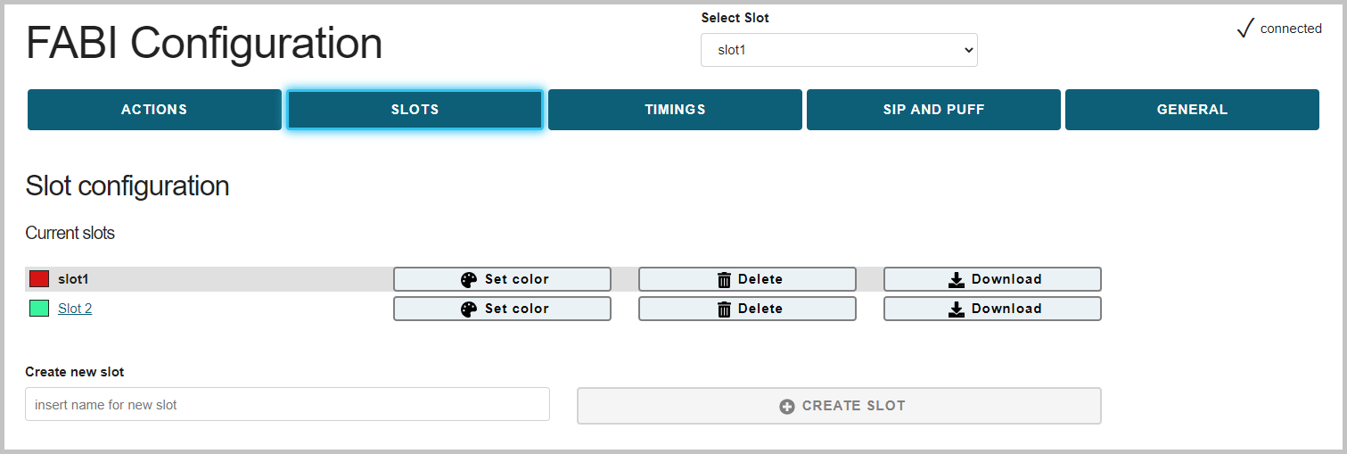
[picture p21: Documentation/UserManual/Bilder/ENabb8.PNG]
Abbildung8


*Figure 9: Creating, changing and deleting configuration slots (*Slots Tab*).

In the top center, the dropdown selection box **Select slot** shows the currently active slot name. By clicking the selection box, all existing slots are shown and the active slot can be changed. 
In *Slot configuration* list you can see all the available slots as well, with the active slot being displayed in bold letters. Here you can change the active slot by clicking one of the inactive slot names. Furthermore, the color of each individual slot can be assigned by clicking **Set color**, which opens a pop-up color selection box. The color which is chosen here will be displayed on the FABI device via a built-in mulicolor led whenever the slot is activated.  ***Note*** that this function is only available in the new version (PCB version) of the FABI system.
A new configuration slot is created by entering a name into the correspnding text field (*"insert name for new slot"*) and clicking **CREATE SLOT**. The settings of the currently active slot are copied to the new slot. The slots can be deleted individually by clicking **Delete**. When **Download** is clicked, the configuration data of the respective slot is downloaded to the PC as a file, which is stored in the download-folder of the web browser. This file can then be used to add individual slots to another configuration. ***Note*** that the complete configuration (all slots) can also be downloaded as as single file, see section "Loading, saving and transferring configurations" below.)

### Loading, saving and transferring configurations

If you scroll further down in the *SLOTS Tab*, you will find functions to backup and restore configurations (Fig. 9). Here you can upload slots from a file: After clicking **Select File**, a local file on the computer can be selected. This file must contain a valid FABI configruation with one or more slots (usually, this file has been saved before to your computer). The whole configuration is applied to the FABI device by clicking **Upload and replace all slots**. This deletes the active configuration in the process. However, by clicking **Show advanced options to upload single slots** instead - desired slots can be selected from the configuration file, which can then be added to the active FABI configuration by clicking **Upload selected slot(s)**.

Saving the current configuration slots of the FABI system is enabled by clicking **Download all slots** (see Figure 10). Here, the entire configuration is downloaded as a single file (.set) to the download-folder of the computer. This file can then be transferred to another computer, and it can be applied to the same or to another FABI device. This allows multiple setups (for example for different users or use cases) to be saved on one computer and to be activated with one click.

***Attention:*** When downloading configuration data, the files are stored in the download-folder of the computer. It makes sense to move these files to another folder afterwards (and eventually rename them) so that they can be easily found and are not accidentally deleted.

### Predefined settings

Demo configuration settings can be selected at the very bottom of the *SLOTS Tab*, in section *Predefined settings* (see Figure 10). These examples offer an overview of the possibilities of the FABI system and serve as a suggestion for your own applications, such as one- or two-button mouse control setups for PC and smart phone or gaming-keys for different applications. A description for the demo configurations can be displayed in a pop-up window, which provides brief information about the button assignments.

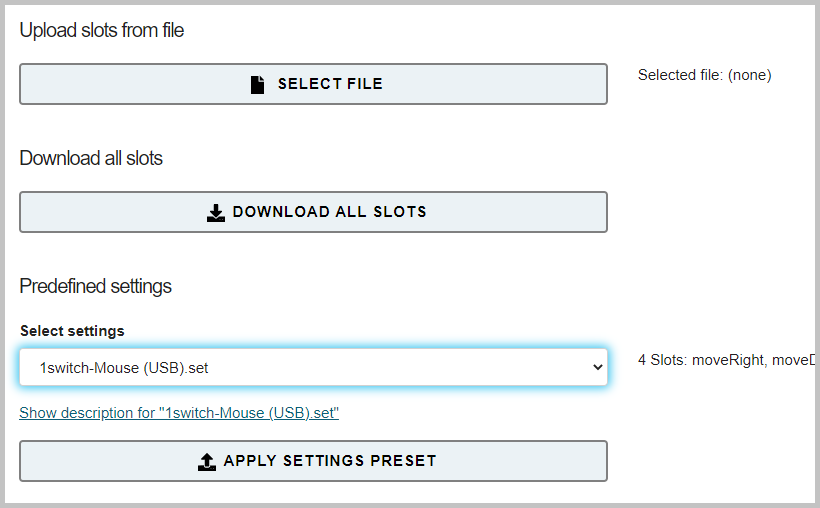
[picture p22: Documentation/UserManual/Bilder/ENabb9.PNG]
Abbildung9


*Figure 10*: Loading and saving configuration settings

## *TIMINGS Tab*: Antitremor and Special Functions

The *TIMINGS Tab* tab can be used to set further parameters for the operation of the FABI system: The *Antitremor settings* allow to specify minimum durations for pressing and releasing the buttons (in milliseconds). These settings can be useful in order to prevent accidental pressing or releasing of buttons due to hand tremor. Furthermore, thresholds can be set for long presses (to create special actions), double presses (to acctivate the next slot), and dell timings for automatic left clicks. All these settings are explained in more detail below.
***Note:*** these settings apply to the active configuration slot, but can be applied to all slots by clicking **Copy config to all slots**.

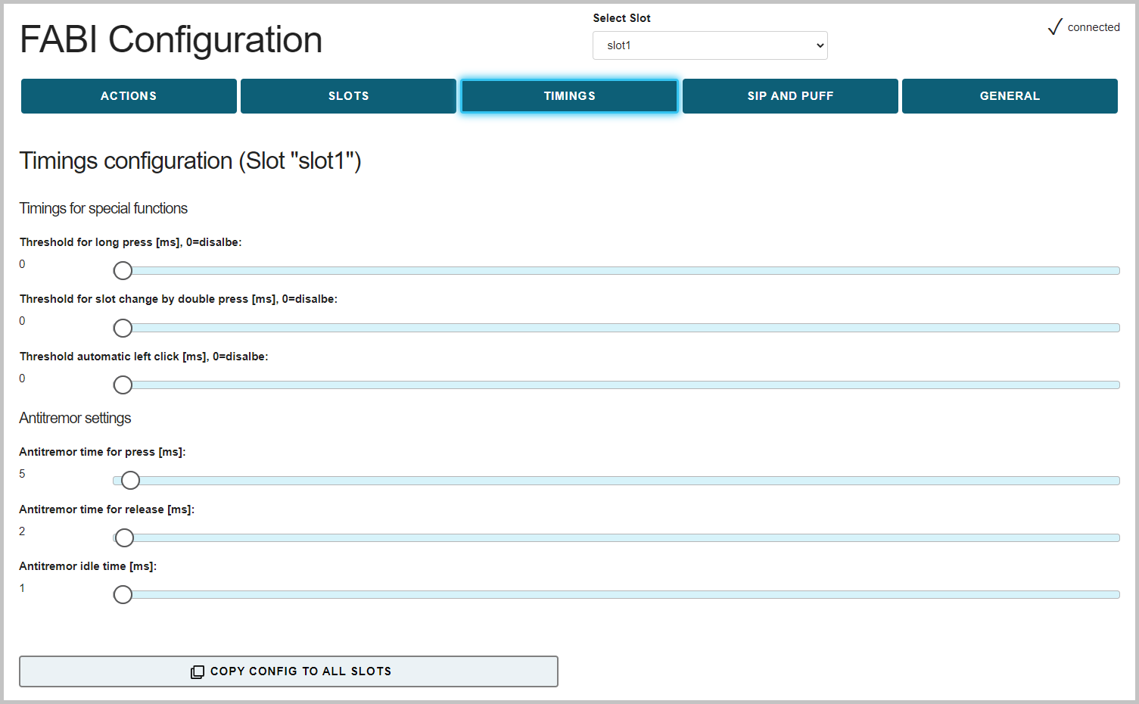
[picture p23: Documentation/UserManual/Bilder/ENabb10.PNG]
Abbildung10
 

*Figure 11*: Screenshot of further settings in the "Timings" tab

### Antitremor settings

The *Antitremor* parameters can be used to define different time periods that are checked by the FABI system when a button is pressed. This can be used to minimize involuntary triggering of buttons in the presence of tremor or fine motor control problems:

- **Antitremor time for press** sets the minimum amount of time a button must be pressed for the action to occur.
- **Antitremor time for release** sets the minimum amount of time a button must be released for the release to be detected.
- **Antitremor idle time** sets the minimum amount of time that must elapse between successive presses of a button.

### Thresholds for special functions

#### Threshold for long press

The **Threshold for long press** specifies a time threshold (in milliseconds) above which a button press is interpreted as a "Long press" and consequently an alternative action can be performed. This is particularly useful if a person can only use a small number of buttons. A long button press can then be used to perform an alternative function (e.g. switching the configuration slot). The corresponding functions can be defined in the *ACTIONS Tab*, function *Button x long press*.
The long press function is *disabled if a threshold value of 0 milliseconds is set*.
Currently, only buttons that are plugged into ports 1, 2 or 3 support the long press function.

#### Using the "Double Press" Function

The **Threshold for slot change by double press** defines the maximum duration of a "double press"-activity in milliseconds. If a fast double press of a button is detected, an *automatic slot change to the next slot* is performed. This is especially useful if a person can only use a single button: Two quick presses can change the function of this button. For example, several keyboard keys could be pressed alternately (e.g. for game control) or the mouse pointer can be moved in different directions using a single button!

#### Threshold automatic left click

This setting makes it possible to generate a left mouse click after the mouse has been moved (dwell clicking). If the selected time period (in milliseconds) elapses without further mouse movements, the left mouse click will be generated automatically. This allows complete control of a mouse pointer with a small number of buttons or (in combination with the automatic slot change function) with only one button. *A value of 0 milliseconds disables the automatic click function*.

## *SIP AND PUFF Tab*: Using a Pressure Sensor

If an analog pressure sensor (optional!) is connected to the FABI system, actions for Sip and Puff (suck and blow) can be defined. The analog voltage value must be connected to the solder contact A0 of the microcontroller board. Furthermore, the sensor needs the correct supply voltage (connect 5V and GND correctly).

In the *SIP AND PUFF Tab*, corresponding threshold values for the strength of sipping or puffing can be set. In the *ACTIONS Tab*, corresponding actions can be selected that can be triggered by these activities. The idle value of the sensor (when neither sipping nor puffing is performed) is in the middle of the value range, around 512.

***Note:*** these settings apply to the active configuration slot, but can be applied to all slots by clicking **Copy config to all slots**.

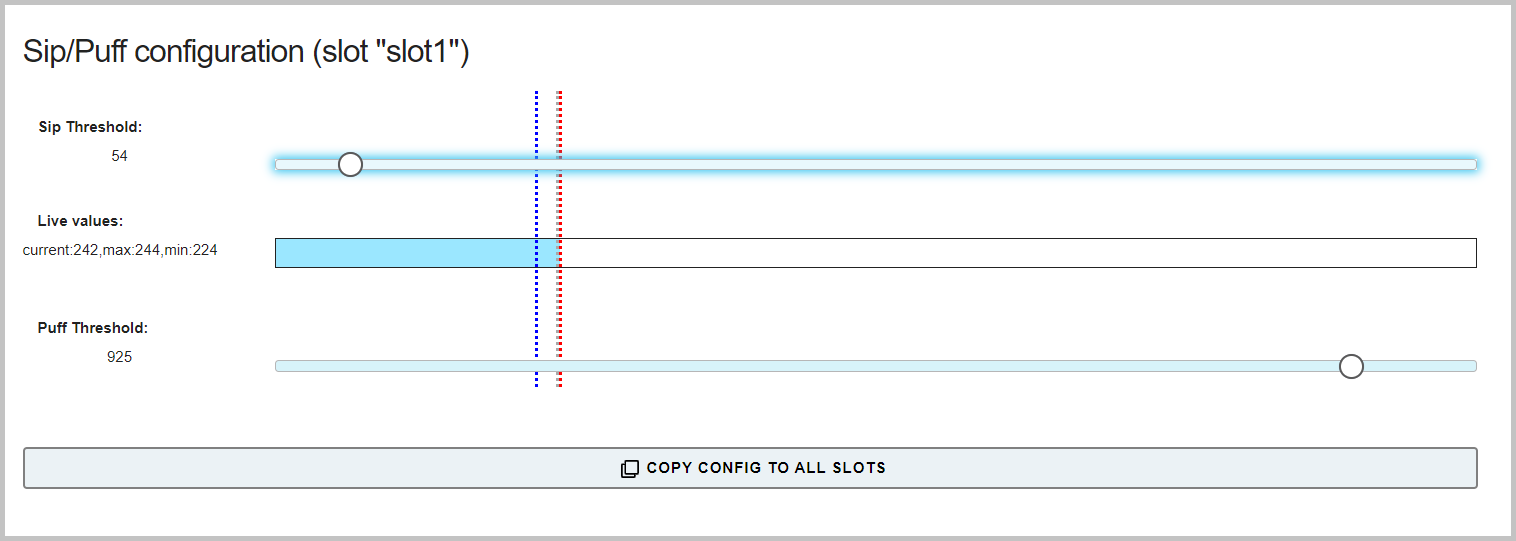
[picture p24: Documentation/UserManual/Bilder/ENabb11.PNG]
Abbildung11


*Figure 12*: Screenshot of the settings for sip and puff thresholds

## *GENERAL Tab*: Bluetooth and Firmware Options

In the *GENERAL Tab*, the Bluetooth settings can be adjusted and the main module firmware and Bluetooth module firmware can be updated.

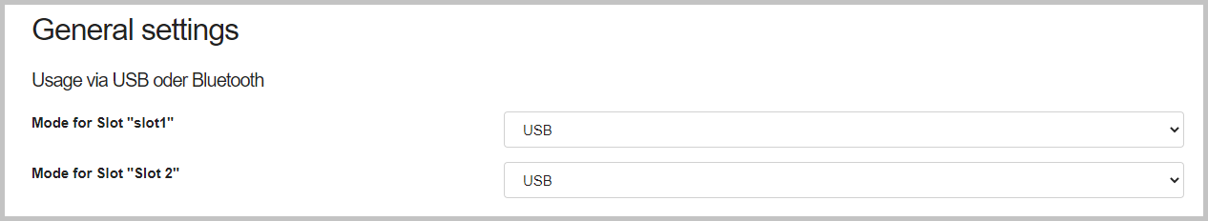
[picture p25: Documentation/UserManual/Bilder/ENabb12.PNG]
Abbildung12
 

*Figure 13*: Screenshot of USB/BT settings in the "GENERAL" tab

### USB Mode / Bluetooth Mode

The optional Bluetooth module (hardware add-on) allows keyboard- and mouse actions to be sent to a connected ("paired") Bluetooth-enabled device (such as a smartphone or tablet computer). The **Mode for Slot x** selection defines whether the mouse and keyboard actions shall be generated via USB, Bluetooth or both (see Figure 13):

***Note:*** The USB/Bluetooh mode selection is only useful if the optional Bluetooth add-on module is connected to the FABI device (see section "Using the Bluetooth module"). 
Since this setting is defined per configuration slot, the same FABI device can be used e.g. to control a laptop via USB and a smartphone/tablet via Bluetooth. Switching control between those devices is done by simply changing the active slot.

### Overwrite / update firmware

Pressing this button will attempt to install the latest software (firmware) for the FABI main module into the microcontroller. This process may take a few minutes. To the left of the button, the version number of the installed firmware and the most recent available version are displayed.

### Reset to default configuration, key combinations

At the bottom of the *GENERAL Tab* you will find the button for resetting the FABI device to the default settings. This is useful if the current settings cause problems with the use of the device. Furthermore, the keyboard shorcuts for switching tabs are displayed here.

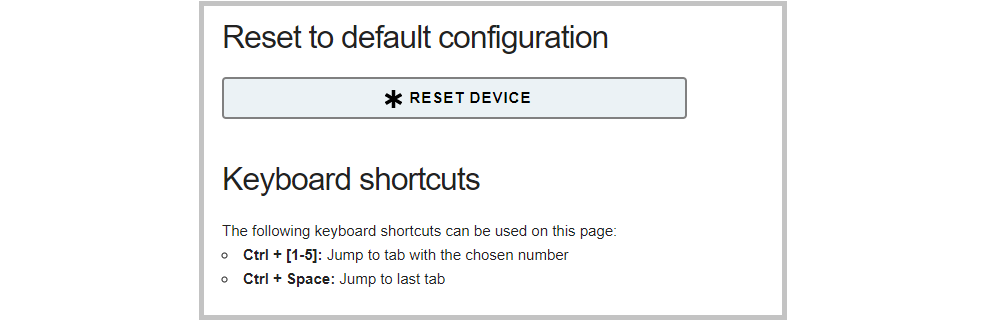
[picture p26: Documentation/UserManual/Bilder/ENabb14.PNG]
Abbildung14
 

*Figure 15*: Reset device, keyboard shortcuts

**Have fun trying out and creating your own FABI configurations!**

## Appendix

### Supported Macro commands:

| **Abbreviation** | **Function**                                                                                                                   | **example**                                                                                 |
| ---------------- | ------------------------------------------------------------------------------------------------------------------------------ | ------------------------------------------------------------------------------------------- |
| CL               | click left mouse button                                                                                                        |                                                                                             |
| CR               | click right mouse button                                                                                                       |                                                                                             |
| CM               | click middle mouse button                                                                                                      |                                                                                             |
| CD               | click double with left mouse button                                                                                            |                                                                                             |
| HL               | hold the left mouse button                                                                                                     |                                                                                             |
| HR               | hold the right mouse button                                                                                                    |                                                                                             |
| HM               | hold the middle mouse button                                                                                                   |                                                                                             |
| TL               | toggle left mouse button                                                                                                       | changes the state of the mouse button                                                       |
| TM               | toggle middle mouse button                                                                                                     |                                                                                             |
| TR               | toggle right mouse button                                                                                                      |                                                                                             |
| RL               | release the left mouse button                                                                                                  |                                                                                             |
| RR               | release the right mouse button                                                                                                 |                                                                                             |
| RM               | release the middle mouse button                                                                                                |                                                                                             |
| WU               | move mouse wheel up                                                                                                            |                                                                                             |
| WD               | move mouse wheel down                                                                                                          |                                                                                             |
| MX `<int>`       | move mouse in x direction                                                                                                      | MX 4 -> moves cursor 4 pixels to the right                                                  |
| MY `<int>`       | move mouse in y direction                                                                                                      | MY -10 -> moves cursor 10 pixels up                                                         |
| RO `<int>`       | rotate stick orientation                                                                                                       | RO 180 -> flips x and y movements of stick/mouthpiece                                       |
| KW `<string>`    | keyboard write string                                                                                                          | KW Hello! -> writes "Hello!" on the keyboard                                                |
| KP `<string>`    | key press: Press keyboard keys (once). Keys are identified by keyboard shortcuts (see list below)                              | KP KEY_UP -> presses the "Cursor-Up" key; KP KEY_CTRL KEY_ALT KEY_DELETE presses all 3 keys |
| KH `<string>`    | key hold: hold keyboard keys                                                                                                   | sKH KEY_LEFT -> holds the "Cursor-Left" key                                                 |
| KT `<string>`    | key toggle: toggle keyboard keys; the key will remain pressed until "AT KT" command is sent again or a "AT KR" command is sent | KT KEY_DOWN -> toggles the "Cursor-Down" key                                                |
| KR `<string>`    | key release                                                                                                                    | KR KEY_UP -> releases the "Cursor-Up" key                                                   |
| RA               | releases all = Release all currently pressed keys and mouse buttons                                                            |                                                                                             |
| WA `<int>`       | wait a certain number of milliseconds                                                                                          | WA 100 -> waits 100 milliseconds                                                            |
| NE               | next slot: load next slot                                                                                                      |                                                                                             |
| LO `<string>`    | Load slot per name, changes to the given slot                                                                                  | LO mouse                                                                                    |
| NC               | No command                                                                                                                     |                                                                                             |

### Supported Key Identifiers:

| **Supported KEY Identifiers:**                                                                                                                                                                                         |
| ---------------------------------------------------------------------------------------------------------------------------------------------------------------------------------------------------------------------- |
| **Letters**                                                                                                                                                                                                            |
| KEY_A  KEY_B  KEY_C  KEY_D  KEY_E  KEY_F  KEY_G  KEY_H  <br/>KEY_I  KEY_J  KEY_K  KEY_L  KEY_M  KEY_N  KEY_O  KEY_P  <br/>KEY_Q  KEY_R  KEY_S  KEY_T  KEY_U  KEY_V  KEY_W  KEY_X KEY_Y KEY_Z                           |
| **Digits**                                                                                                                                                                                                             |
| KEY_1  KEY_2  KEY_3  KEY_4  KEY_5  KEY_6  KEY_7  KEY_8  KEY_9  KEY_0                                                                                                                                                   |
| **Function keys**                                                                                                                                                                                                      |
| KEY_F1  KEY_F2  KEY_F3  KEY_F4  KEY_F5  KEY_F6  KEY_F7  KEY_F8  KEY_F9  KEY_F10  <br/>KEY_F11  KEY_F12  KEY_F13  KEY_F14  KEY_F15  KEY_F16  KEY_F17  KEY_F18  KEY_F19 <br/>KEY_F20  KEY_F21  KEY_F22  KEY_F23  KEY_F24 |
| **Navigation keys**                                                                                                                                                                                                    |
| KEY_UP  KEY_DOWN  KEY_LEFT  KEY_RIGHT  KEY_TAB  KEY_PAGE_UP  KEY_PAGE_DOWN <br/>KEY_HOME  KEY_END                                                                                                                      |
| **Special keys**                                                                                                                                                                                                       |
| KEY_ENTER  KEY_SPACE  KEY_BACKSPACE  KEY_DELETE  KEY_INSERT  KEY_ESC  KEY_NUM_LOCK<br/>KEY_SCROLL_LOCK  KEY_CAPS_LOCK  KEY_PAUSE<br/>                                                                                  |
| **Tasten für alternative Funktionen**                                                                                                                                                                                  |
| KEY_SHIFT  KEY_CTRL  KEY_ALT  KEY_RIGHT_ALT  KEY_GUI  KEY_RIGHT_GUI                                                                                                                                                    |

### Further links and software recommendations

The FABI Button Interface can be applied as an alternative input system for a wide range of applications - including computer/smartphone control, AAC software/device control, accessible gaming and educational software. Depending on the number of buttons that can be used by a person, standard programs with mouse / keyboard input can also be used without further adaptation.

If motor skills are very limited, special applications allow many activities by using just a single switch! Some interesting resources are presented below:

#### AsTeRICS and AsTeRICS Grid

Other open source developments of the [AsTeRICS Foundation](https://www.asterics-foundation.org) allow versatile use of button interfaces. The [AsTeRICS](https://www.asterics.eu) system is a construction kit for assistive technologies; it also offers examples for 1-button solutions for computer control. [AsTeRICS Grid](https://grid.asterics.eu) is a flexible system for AAC (Augmentative and Alternative Communiication) that can be used with a single switch.

#### SpecialEffect.org

The non-profit organization SpecialEffect ([www.specialeffect.org.uk](https://www.specialeffect.org.uk)) is dedicated to spreading accessible gaming in the UK and makes special adaptations for people with disabilities.

#### BLTT.org

The Better Living Through Technology website ([bltt.org/introduction-to-switch-access](https://bltt.org/introduction-to-switch-access)) provides useful information for button-based use of computers and links to many software tools.

#### OneSwitch.org

At [www.oneswitch.org.uk](https://www.oneswitch.org.uk/) Barrie Ellis has collected a wealth of tips and information for single-switch gaming and special adaptations for button controls of computer games. Of particular interest are the game library, the one-switch pulse system, and the use of game consoles via controller adapters like the "Titan-Two".

#### Click2Speak

[Click2Speak](https://www.click2speak.net) is a flexible on-screen keyboard for Windows that provides additional useful features - such as a mouse click selection box.

## Contact Information

**AsTeRICS Foundation**

Webpage: <https://www.asterics-foundation.org>

Email: <office@asterics-foundation.org>

## Disclaimer

The University of Applied Sciences Technikum Wien and the AsTeRICS Foundation do not assume any warranty or liability for the functionality of the hardware/software modules or the correctness of the documentation.

Furthermore, the FH Technikum Wien and the AsTeRICS Foundation are not liable for any damage to health caused by the use of the provided hardware/software modules. 
The use of the provided modules and information is at your own risk!

## Acknowledgements

We would like to thank Miriam Brenner, Fabian Schiegl and Fanny Peternell for their support in writing this manual and Andreas Fußthaler for developing the PCB & case of the previous version.

This project was financially supported by the City of Vienna (Magistratsabteilung 23 für Wirtschaft, Arbeit und Statistik, MA 23) (project number 14-02, 18-04).

Abbildung18

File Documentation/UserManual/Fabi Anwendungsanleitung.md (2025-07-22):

# FABI - Anwendungsanleitung

FabiLogo

FabiFoto

____

# Willkommen bei FABI

FABI - das „Flexible Assistive Button Interface“ - ermöglicht es, bis zu fünf Taster (Buttons) an einen Computer oder ein Tablet/Smartphone anzuschließen und dadurch Maus-, Keyboard- oder Joystick-Aktionen auszulösen sowie andere Aktionen auszuführen. Ein konfiguriertes FABI-Modul kann mit jedem Computer (Windows, Linux oder Mac) oder mobilem Gerät (iPad/iPhone, Android), ohne Installation von spezieller Software verwendet werden, weil sich das FABI-Modul beim Anschließen an den Computer wie eine gewöhnliche Computermaus bzw. eine Tastatur verhält. Menschen, für die herkömmliche Eingabegeräte nicht geeignet sind, können dadurch Computerspiele spielen, im Internet surfen, E-Mails schreiben und vieles mehr.

[TOC]

## Einleitung

Das FABI-System kann mit kommerziell erhältlichen Schaltern, günstigen Arcade-Buttons oder auch mit selbstgebauten elektrischen Kontakten verwendet werden. FABI besteht aus einem Hardware-Modul (einem kostengünstigen Mikrocontroller, der als Computermaus oder Tastatur fungiert), weiteren optionalen Modulen und Sensoren (z.B. Sip/Puff-Drucksensor) und einer grafischen Konfigurationsoberfläche zum Einstellen von gewünschten Funktionen („FABI-Konfigurationsmanager“). 

FABI ist als Open Source Bausatz (inkl. entsprechender Bauanleitung für die Hardware) verfügbar und wurde im Rahmen des AsTeRICS Academy Projektes der FH Technikum Wien entwickelt. 2017 wurde die gemeinnützige Organisation AsTeRICS Foundation gegründet, um derartige Technologien und Systeme weiterzuentwickeln und kostengünstig zur Verfügung stellen zu können: [www.asterics-foundation.org](https://asterics-foundation.org/).

Alle Softwaremodule, die Hardware-Designdateien und die Dokumente für die Anleitungen sind unter freien Open Source Lizenzen verfügbar und können kostenlos verwendet und verändert werden. Wir haben uns bemüht, preisgünstigste Komponenten auszuwählen und dennoch keine Kompromisse bei Funktionalität und Flexibilität zu machen – was FABI zu einer erschwinglichen Tasterschnittstelle mit umfangreichen Möglichkeiten macht!

Der **FABI-Konfigurationsmanager** wird benötigt, um die Funktionen der Taster / Buttons festlegen zu können. Nachdem eine Konfiguration im FABI-System gespeichert wurde, bleibt sie dort erhalten und das FABI-System kann zur Steuerung unterschiedlicher Geräte verwendet werden (z.B. Windows-PC, Mac-Computer, Tablet oder Smart-Phone mit USB- oder Bluetooth-Anschluss). Der Konfigurationsmanager wird erst wieder benötigt, wenn Einstellungen geändert werden sollen.

Der Konfigurationsmanager wird im Chrome oder Edge Web-Browser (Safari oder Firefox funktionieren nicht) geöffnet und ist unter folgender Adresse zu finden: [fabi.asterics.eu](https://fabi.asterics.eu/index_fabi.htm). Untenstehend in Abbildung 1 sehen sie die Startseite. Wenn Sie auf den Button VERBINDEN ZU FABI (ÜBER USB ANGESCHLOSSEN) klicken, so wird in der Auswahlbox noch kein Kommunikationsanschluss (COM Port) auswählbar sein, sofern Sie das FABI Modul noch nicht mittels USB-Stecker mit dem Computer verbunden haben. 

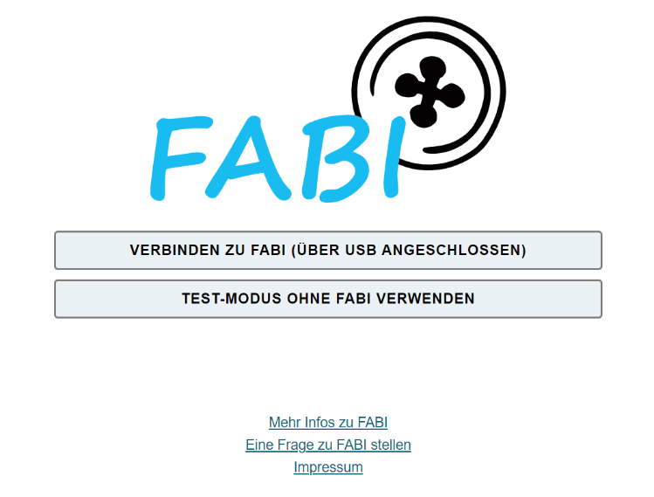
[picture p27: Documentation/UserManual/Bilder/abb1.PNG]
Abbildung1


*Abbildung 1*: Startseite des Konfigurationsmanagers

#### Anschließen des USB-Micro Kabels

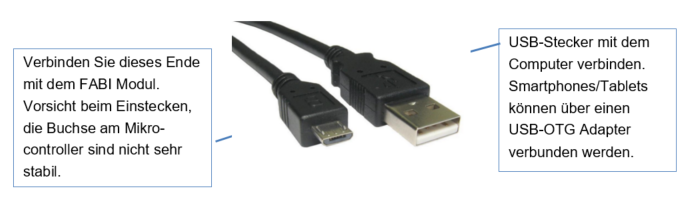
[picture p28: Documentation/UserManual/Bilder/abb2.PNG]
Abbildung2


*Abbildung 2*: Anschließen des USB-Micro Kabels

#### Das FABI-Gerät verbinden

Um die Funktionen der Web-Konfiguration zu verwenden, folgen Sie den nachfolgenden Schritten:

1. Vergewissern Sie sich, dass das FABI- Gerät mit dem Computer verbunden ist. 
2. Danach sollte in einem Pop-Up Fenster ein Kommunikations-Anschluss (COM Port) mit bestimmter Nummer (z.B. COM4) auswählbar sein. Klicken Sie diesen Eintrag an und drücken Sie danach auf *Verbinden*. (Nach dem Ausstecken des FABI-Moduls sollte der COM Port wieder verschwinden.) 
3. **Sollten Sie nicht die Benutzeroberfläche des FABI Konfigurationsmanagers wie in Abbildung 3 sehen können, so öffnen Sie die Website erneut und wählen Sie einen anderen COM-Port in der aufpoppenden Auswahlbox. Danach klicken Sie erneut auf *Verbinden*.** 

## Verwendung des Konfigurationsmanagers

Nachdem Sie mit dem Kommunikations-Anschluss des FABI Systems verbunden sind, sehen Sie nun die Benutzeroberfläche des FABI Konfigurationsmanagers (Abbildung 3).

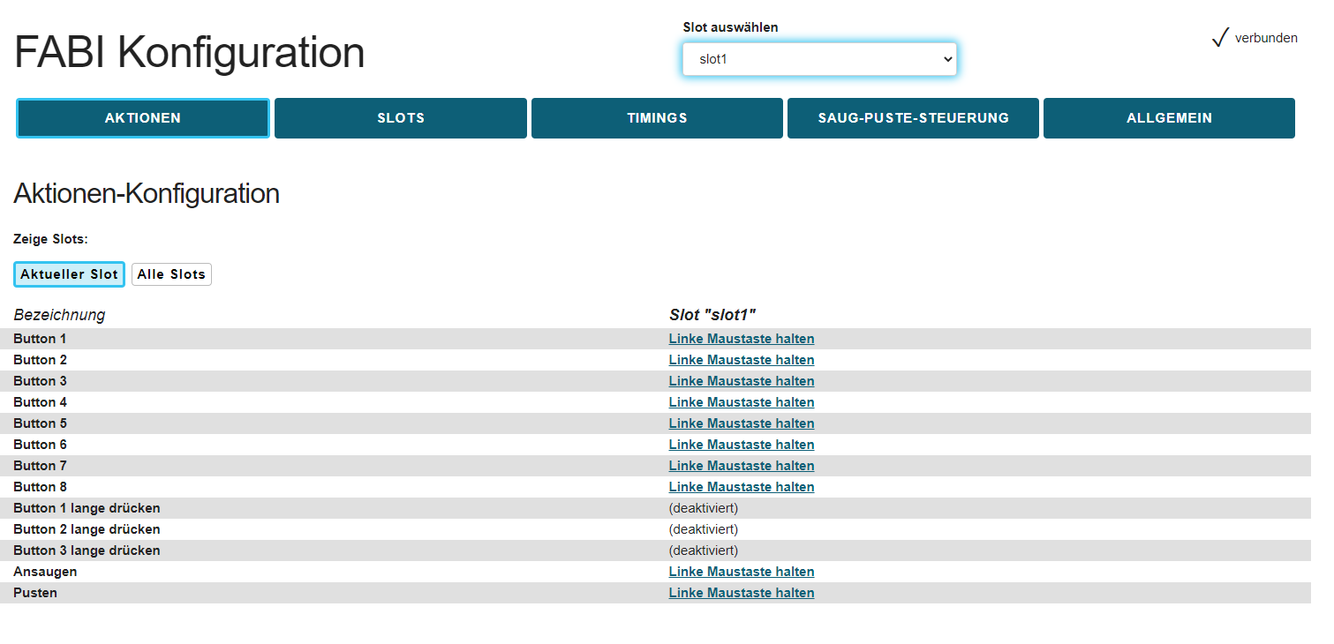
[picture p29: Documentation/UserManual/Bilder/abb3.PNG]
Abbildung3
 

*Abbildung 3*: FABI-Konfigurationsmanager Benutzeroberfläche

#### Port Status

Der Portstatus rechts oben zeigt an, ob das FABI-Gerät aktuell mit dem Konfigurationsmanager verbunden ist. Die eingestellten Funktionen der Taster können nur dann ins Gerät übertragen werden, wenn als Port Status „Verbunden” angezeigt wird. Ist das Gerät nicht mehr verbunden, gelangen Sie wieder auf die Startseite.

#### Einstellungen speichern

Die getroffenen Einstellungen werden automatisch gespeichert und sind sofort im FABI-Gerät aktiv. **Die Konfigurationen bleiben auch dann erhalten, wenn das FABI System vom USB-Kabel bzw. von der Stromversorgung getrennt wird.** 

### Zuweisung der Taster-Funktionen (Reiter "AKTIONEN")

Im Reiter **AKTIONEN** können bis zu 5 Taster mit verschiedenen Funktionen belegt werden. Die Funktionen beinhalten etwa verschiedene Mausklicks, Mausbewegungen, Betätigung des Maus-Scrollrads oder von Keyboard-Tasten. Sie können die Aktion für den jeweiligen Taster ändern, indem Sie rechts vom gewünschten Button auf die unterstrichene (momentan aktive) Aktion klicken - siehe rotes Viereck in Abbildung 4.1. Dann erscheint ein Fenster, wo die gewünschte Aktions-Kategorie (hier: Maus) und die gewünschte Aktion ausgewählt werden kann (hier: Linke Maustaste halten). *Anmerkung:* Sollten mehr als 8 Taster benötigt werden, können mehrere FABI-Module parallel betrieben werden.

Abbildung4.1 

*Abbildung 4.1*: Aktion für Taster auswählen/ändern

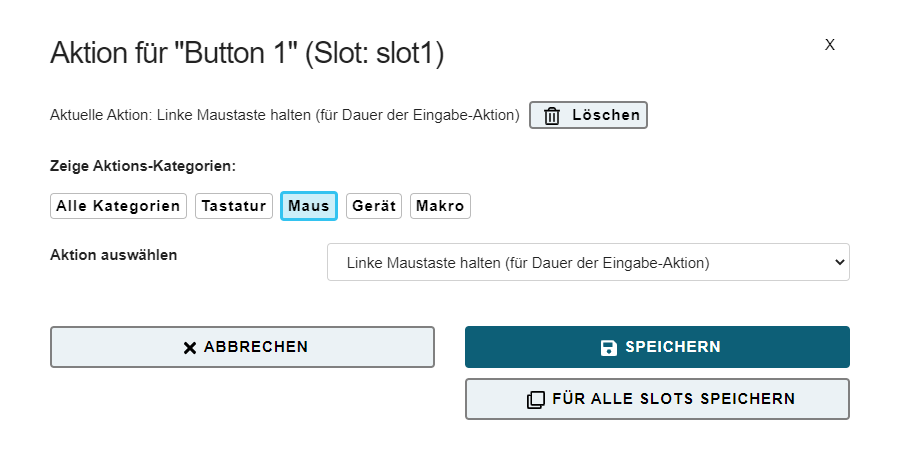
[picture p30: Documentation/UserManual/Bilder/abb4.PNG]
Abbildung4.2
 

*Abbildung 4.2*: Aktion für Taster auswählen (hier: Button 1)

#### Aktionskategorie Maus

##### Linke/Rechte/Mittlere Maustaste halten (für Dauer der Eingabe-Aktion)

Durch diese Funktionen bleibt die linke, rechte oder mittlere Maustaste gedrückt, solange der Taster gehalten wird (zum Beispiel, um eine Datei zu verschieben, ist es nötig, die linke Maustaste gedrückt zu halten). 

##### Klick linke/rechte/mittlere Maustaste

Mit diesen Funktionen kann einen Klick der linken, rechten oder mittleren Maustaste durch die Betätigung des Tasters ausgeführt werden. **Anmerkung**: ein Klick besteht aus drücken & loslassen der entsprechenden Maustaste, beides passiert kurz hintereinander nach der Betätigung des Buttons!

##### Doppelklick linke Maustaste

Ein Doppelklick der linken Maustaste ist zum Beispiel zum Öffnen einer Datei notwendig. Das Ausführen von schnellen Mausklicks kann jedoch für manche NutzerInnen schwierig sein. Durch das Zuweisen dieser Funktion kann ein Doppelklick durch einen einfachen Druck auf den Taster durchgeführt werden. 

##### Drücken oder Loslassen linke/rechte/mittlere Maustaste (wechseln)

Mit diesen Funktionen wird der Zustand der linken, rechten oder mittleren Maustaste geändert, wenn der Taster gedrückt wird. Beachten Sie, dass die Maustaste solange gedrückt bleibt, bis der Taster ein weiteres Mal gedrückt wird!

##### Nach unten / nach oben scrollen

Die Funktionen „Nach oben scrollen” und „nach unten scrollen” erzeugen durch den Taster Aktivitäten mit dem ein Scrollrad der Computermaus. Das Auslösen der “Nach oben scrollen” Funktion führt dazu, dass aufwärts gescrollt wird, bei der „Nach unten scrollen“ Funktion wird abwärts gescrollt (nützlich etwa zum Lesen von Dokumenten oder Webseiten).

##### Maus horizontal / vertikal bewegen – Mausbewegung in x- oder y-Richtung

Die „Maus horizontal bewegen (x-Achse)” und „Maus vertikal bewegen (y-Achse)” Funktionen erzeugen Computermausbewegungen entlang der gewählten Achsen. Für diese Funktionen können im darunter erscheinenden Feld Geschwindigkeitsparameter festgelegt werden. Beim Drücken des Tasters wird der Mauszeiger bis zu dieser maximalen Geschwindigkeit (zb. 20 oder -20) beschleunigt.

*Ein positiver Wert für die X-Richtung bewegt den Mauszeiger nach rechts.
Ein negativer Wert für die X-Richtung bewegt den Mauszeiger nach links.
Ein positiver Wert für die Y-Richtung bewegt den Mauszeiger nach unten.
Ein negativer Wert für die Y-Richtung bewegt den Mauszeiger nach oben.*

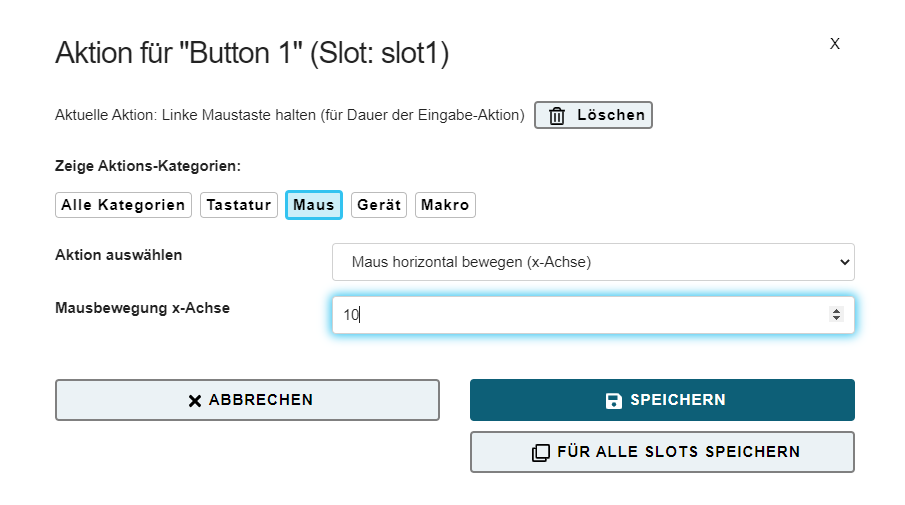
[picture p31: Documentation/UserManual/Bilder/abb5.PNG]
Abbildung5
 

*Abbildung 5*: Screenshot der "Maus horizontal bewegen (x-Achse)"-Funktion bzw. Geschwindigkeitseinstellung

#### Aktionskategorie Tastatur

##### Taste(n) halten (für Dauer der Eingabe-Aktion)

Mit der Funktion "Taste(n) halten (für Dauer der Eingabe-Aktion)" können gewünschte Tasten der Computertastatur gehalten werden, sobald der Taster gedrückt wird. Die vorher ausgewählte Tastaturtaste(n) werden so lange gedrückt, wie der Taster gehalten wird. Die Tastenauswahl funktioniert wie bei dem Befehl "Tasten drücken" beschrieben.

##### Taste(n) drücken + wieder loslassen

Die „Taste(n) drücken + wieder loslassen ”-Funktion ermöglicht es, gewünschte Tasten (auch Kombinationen) des Computerkeyboards auszulösen, sobald der Taster gedrückt wird. Die Keyboard-Tasten werden gedrückt und sofort wieder losgelassen (also nicht so lange gehalten, wie der Taster gehalten bleibt). 

##### Taste(n) drücken oder auslassen (wechseln)

Mit der Funktion "Taste(n) drücken oder auslassen (wechseln)" können gewünschte Tasten auf der Computertastatur ihren Zustand ändern (also gedrückt werden bzw. losgelassen werden), sobald die Taste gedrückt wird. Beachten Sie, dass die Tastaturtaste solange gedrückt bleibt, bis die Taste ein weiteres Mal gedrückt wird! Die Tastenauswahl funktioniert wie bei dem Befehl "Tasten drücken" beschrieben.

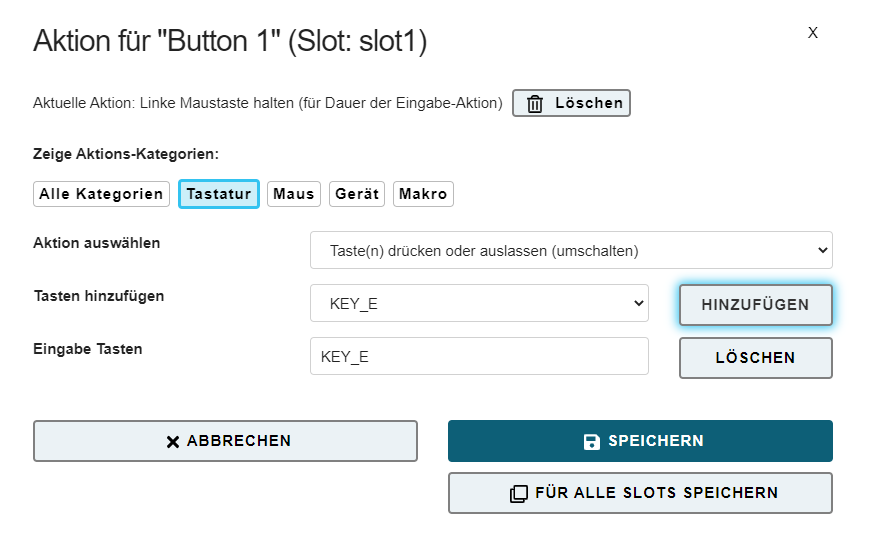
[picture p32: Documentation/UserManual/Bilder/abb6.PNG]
Abbildung6
 

*Abbildung 6*: Screenshot der "Press Key"-Funktion

Die gewünschte Taste kann jeweils aus der Auswahlbox gewählt werden, die links neben „Hinzufügen“ mit dem Pfeil aufklappbar ist. Danach klicken Sie auf „Hinzufügen“ und die Eingabe erscheint auch in der nächsten Zeile („Eingabe Tasten“). Das Beispiel in Abbildung 6 zeigt die Verwendung der Keyboard-Taste “KEY_E” – es wird dadurch bei jedem Druck des Tasters ein kleines „e“ geschrieben. Es ist möglich, auch mehrere Tasten für Tastenkombinationen auszuwählen, die dann gleichzeitig gedrückt/gehalten werden. Alternativ zur einzelnen Auswahl von Tasten aus der Auswahlbox können Tasten bzw. Tastenkombinationen auch automatisch erkannt werden, wenn das Feld "Tasten mit Tastatur eingeben" aktiviert wird. 
Bereits zugewiesene Tasten können durch klicken von „Löschen“ entfernt werden.

**Anmerkung:** Mit „KEY_SHIFT“ können Großbuchstaben verwendet werden. Alle weiteren unterstützen Keyboard-Tastenkürzel finden Sie im [Anhang](https://github.com/asterics/FABI/blob/master/Documentation/UserManual/Markdown/Fabi%20Anwendungsanleitung.md#liste-der-k%C3%BCrzel-f%C3%BCr-keybord-tasten).

##### Schreibe Wort

Die „Write Text”-Funktion ermöglicht es, jedes Mal einen bestimmten Text zu schreiben, wenn der ausgewählte Taster gedrückt wird. Die kann z.B. für die Eingabe von Passwörtern nützlich sein. Wenn Sie „Schreibe Wort“ auswählen, scheint unter dem Dropdown-Menü ein leeres Textfeld auf, klicken Sie dann auf das Textfeld und geben Sie den gewünschten Text ein:

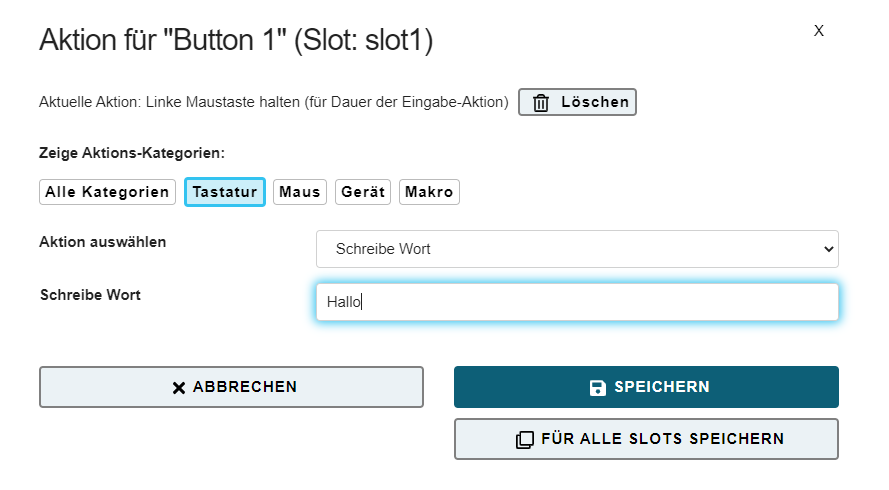
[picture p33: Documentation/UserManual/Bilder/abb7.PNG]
Abbildung7
 

*Abbildung 7*: Screenshot der "Schreibe Wort"-Funktion

#### Aktionskategorie "Joystick"

**Joystick x-/y-/z-Achse/z-Drehung/Regler setzen**
Diese Aktionen können verwendet werden, um einen gewünschten Wert an die Joystick-Achse zu senden. Die wählbaren Joystick-Achsen sind: *X / Y / Z / Z-Drehung / Regler*. Der Joystick wird in die Mittelstellung zurückbewegt, wenn die zugehörige Benutzeraktivität endet.

**Joystick-Button halten (für Dauer der Eingabe-Aktion)**
Diese Aktion kann verwendet werden, um einen gewünschte Joystick-Button zu drücken. Das FLipMouse-Gerät unterstützt 32 Tasten, so dass jeder Wert von 1 bis 32 zulässig ist. Der Joystick-Button wird losgelassen, wenn die zugehörige Benutzeraktivität beendet ist.

**Joystick Hat-Position setzen**
Mit dieser Aktion wird die Ausrichtung des Joystick-"Hats" (in Grad) festgelegt. Erlaubte Werte sind:
*-1, 0, 45, 90, 135, 180, 225, 270, 315*. Der Wert -1 setzt den Hat auf die mittlere Position (Leerlauf). 
Der Joystick-Hat wird in die Mittelstellung zurückbewegt, wenn die zugehörige Benutzeraktivität endet.

#### Aktionskategorie: "Infrarot"

**Infrarot-Kommando abspielen / halten**
Diese Aktion gibt den Infrarot (IR-)Code mit dem angegebenen Befehlsnamen wieder. Die vorhandenen (aufgezeichneten) IR-Befehle können aus dem Dropdown-Menü ausgewählt werden. Die Aktion *Infrarot-Kommando abspielen* sendet den aufgezeichneten Code einmal, während die Aktion *Infrarot-Kommando halten* den Code wiederholt, bis die Benutzeraktivität beendet ist. 

<p align="left" width="100%">
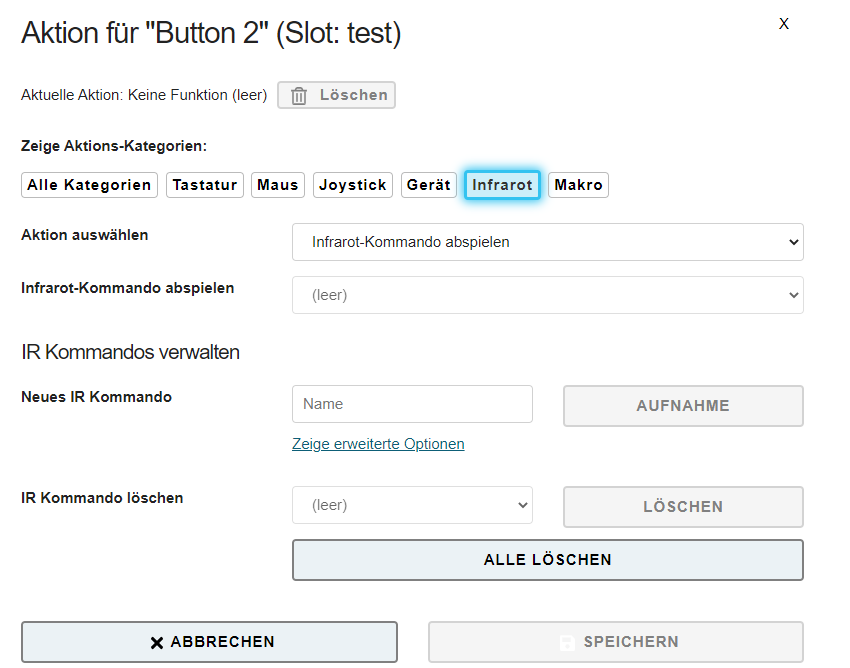
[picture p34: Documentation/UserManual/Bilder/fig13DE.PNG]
    
</p>
*Abbildung 8: Konfigurationsmanager für Infrarot-Aufnahme und -Wiedergabe*

Das FABI verfügt über ein Infrarot-Fernbedienungs-Empfängermodul und eine Hochleistungs-IR-LED, sodass es Fernbedienungscodes vieler in der Unterhaltungselektronik verwendeter Fernbedienungsgeräte aufzeichnen und wiedergeben kann. 

#### Aktionskategorie Gerät

##### Keine Funktion

Wenn „Keine Funktion” im Funktionsmenü ausgewählt wird, dann wird der entsprechede Taster deaktiviert.

##### Nächsten Slot laden – zur nächsten Konfiguration wechseln

Sobald der Taster gedrückt wird, wird der nächste Speicherplatz (Slot) aktiviert. Dadurch können die einzelnen Slots über einen Taster nach der Reihe durchgeschalten werden. Nach der letzten Konfiguration wird automatisch die erste Konfiguration aktiviert. (Diese Aktion ist nur relevant, wenn Sie Konfigurationen in mehreren Speicherplätzen abgelegt haben.)

##### Slot per Name laden – zu Konfiguration mit bestimmtem Namen wechseln

Sobald der Taster gedrückt wird, wird die Konfiguration mit dem angegebenen Namen aktiviert. (Diese Aktion ist nur relevant, wenn Sie Konfigurationen in mehreren Speicherplätzen abgelegt haben.)

#### Aktionskategorie Makro

##### Benutzerdefiniertes Makro – Makrokommandos ausführen

Diese fortgeschrittene Funktion ermöglicht die Ausführung mehrerer Kommandos über entsprechende Kommando-Kürzel, was eine hohe Flexibilität ermöglicht. Die einzelnen Kommandos werden im Textfeld durch Strichpunkte getrennt eingetragen. Kommandokürzel können auch mittels „Befehl hinzufügen“ ausgesucht und dann mit „HINZUFÜGEN“ im Makro hinzugefügt werden. Werden mehrere Befehle hintereinander hinzugefügt, so werden die Strichpunkte automatisch eingetragen.
Beispiel: Das Makrokommando MX 10; WA 500; KP KEY_A; bewegt den Mauscursor 10 Punkte nach rechts, wartet dann 500 Millisekunden und drückt dann die Keyboardtaste „A“.
**Anmerkung**: Die möglichen Befehle, die hinzugefügt werden können, werden aufgelistet, sobald der Pfeil rechts gedrückt wird. Die möglichen Kommando- und Tastenkürzel können aber auch händisch in der Zeile „Makro“ eingegeben werden, und sind auch am [Ende dieser Dokumentation](https://github.com/asterics/FABI/blob/master/Documentation/UserManual/Markdown/Fabi%20Anwendungsanleitung.md#liste-der-unterst%C3%BCtzten-makrokommandos) zu finden.

### Verwendung der Speicherplätze (Reiter "SLOTS")

Verschiedene Funktionsbelegungen der Buttons können in bis zu 10 Speicherplätzen (***Konfigurations-Slots***) abgelegt werden. Diese Speicherplätze können auch während des Betriebes gewechselt werden, z.B. über einen beliebigen Taster. Sobald das FABI-Gerät über das USB Kabel mit Strom versorgt wird, wird der erste Speicherplatz (Slot) automatisch geladen und aktiviert.

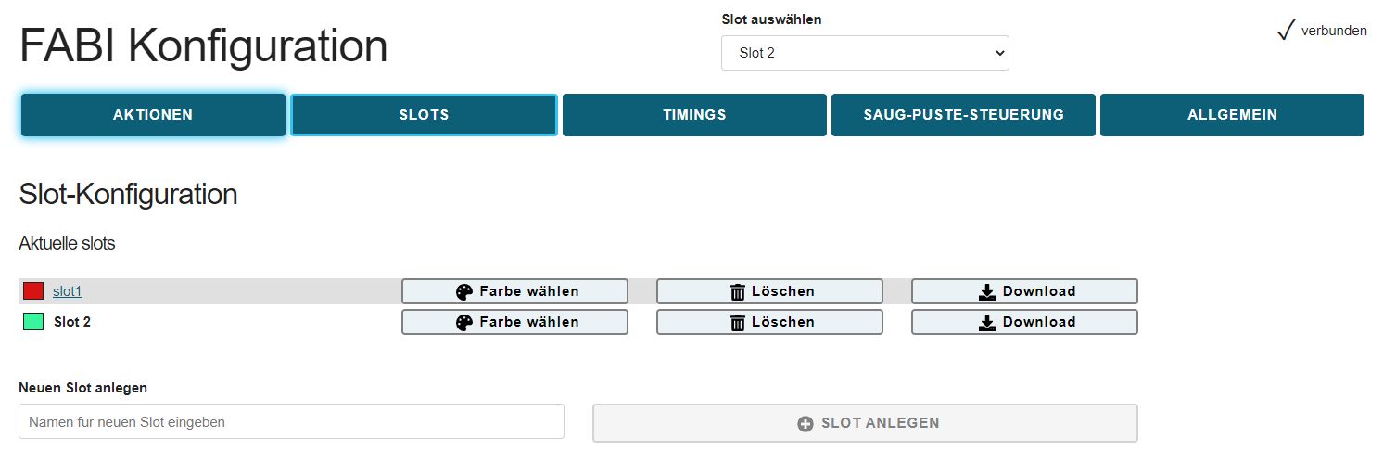
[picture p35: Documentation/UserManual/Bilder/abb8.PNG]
Abbildung9


*Abbildung 9: Anlegen, Wechseln und Löschen von Speicherplätzen (“Slots“)*

Ein neuer Speicherplatz wird im Reiter **SLOTS** durch Klicken von „**SLOT ANLEGEN**“ erzeugt. Dabei werden die Einstellungen des aktuell akiven Slots übernommen (kopiert). Mit einem vorhergehenden Klick in das Textfeld kann ein beliebiger Name für den neuen Slot vergeben werden. Mittig oben befindet sich ein Dropdown-Menu mit der Überschrift **„Slot auswählen“**. Wenn Sie auf der rechten Seite des Textfeldes auf den Pfeil klicken, öffnet sich das Dropdown-Menu, das bereits gespeicherte Slots anzeigt und wo diese ausgewählt werden können. In der Liste **Slot-Konfiguration** sehen Sie alle verfügbaren Slots, wobei der aktive Slot in fetter Schift dargestellt wird. Hier können Sie auch die Farbe wählen, die beim Aktivieren eines Slots am FABI-Gerät dargestellt wird. Die Slots können bei Bedarf einzeln gelöscht oder auf den Computer heruntergeladen werden.

#### Auswahl einer Farbe für die Konfiguration

Durch das Anklicken des Feldes “Farbe wählen” rechts neben dem entsprechenden Slot im Reiter **SLOTS** erscheint ein Farbwahl-Dialog am Bildschirm. Hier kann eine gewünschte Farbe selektiert werden. Die Farb-Leichtdiode im FABI-Gehäuse nimmt diese Farbe an, sobald die entsprechende Konfiguration aktiviert wird. So lassen sich allen Konfigurations-Slots charakteristische Farben zuordnen. **Hinweis**: Diese Funktion ist nur in der neuen Version (PCB Version) des FABI-Systems verfügbar.

#### Wahl der Übertragung (Bluetooth / USB)

Für jeden einzelnen Slot kann ausgewählt werden ob bei dieser Konfiguration die Aktionen über USB (z.B: Computer) oder über Bluetooth (z.B. Smartphone) ausgeführt werden.

#### Slot Download / löschen

Mit diesen Buttons kann jeder einzelne Slot gelöscht werden sowie für die Weitergabe oder als Backup einzeln heruntergeladen werden.

#### Laden, Speichern und Übertragen von Konfigurationen

Wenn Sie im Reiter **SLOTS** weiter nach unten scrollen, finden Sie die Funktionen für das Slot-Backup. Hier können Sie etwa Slots aus einer Datei hochladen: Dabei kann nach dem Anklicken von „Datei auswählen“ eine lokale Datei am Computer ausgewählt werden, die Konfigurationseinstellungen beinhaltet. Diese Einstellungen werden durch klicken von "Alle Slots hochladen und ersetzen" gesamt ins FABI-Gerät übertragen, dabei wird die aktuelle Konfiguration gelöscht. Es können jedoch auch einzelne Slots aus der Konfigurationsdatei zur aktiven FABI-Konfiguration hinzugefügt werden. Dafür werden nach dem Einblenden der erweiterten Optionen gewünschte Slots ausgewählt und durch klicken von "Gewählte(n) Slots hochladen" ins Gerät übertragen.

Das Speichern der aktuellen Konfigurationseinstellungen des FABI-Systems in eine Datei wird durch klicken von „Alle Slots herunterladen“ ermöglicht (siehe Abbildung 10). Hierbei wird die gesamte Konfiguration als Datei (.set) auf dem Computer gespeichert. Diese Einstellungsdatei kann anschließend auf dasselbe oder ein anderes FABI-Gerät übertragen werden. Dadurch können mehrere Setups (zum Beispiel für unterschiedliche AnwenderInnen oder Anwendungsfälle) auf einem Computer gespeichert werden und durch einen Klick aktiviert werden.

**Achtung**: Beim Herunterladen einzelner Slots oder der gesamten Einstellungen werden die Dateien im Download-Verzeichnis des Web-Browsers abgelegt. Es ist sinnvoll, die Dateien anschließend in ein anderes Verzeichnis zu legen, damit sie leicht auffindbar sind und im Download-Verzeichnis nicht versehentlich gelöscht werden.

#### Demo-Voreinstellungen

Im Reiter **SLOTS** können ganz unten im Bereich "Demo-Voreinstellungen" (siehe Abbildung 10) vorbereitete Konfigurationseinstellungen ausgewählt werden. Diese bieten einen Überblick auf die Möglichkeiten des FABI-Systems und dienen als Anregung für eigene Anwendungen, etwa eine 1-Tasten-Maussteuerung, eine 2-Button-Steuerung von Computer und Smart-Phone oder eine Verwendung von Maus- und Cursortasten mit mehreren Buttons. Eine Beschreibung für die Demo-Konfigurationen kann angezeigt werden und bietet Kurzinformationen über die Funktionen bzw. Tastenbelegung.

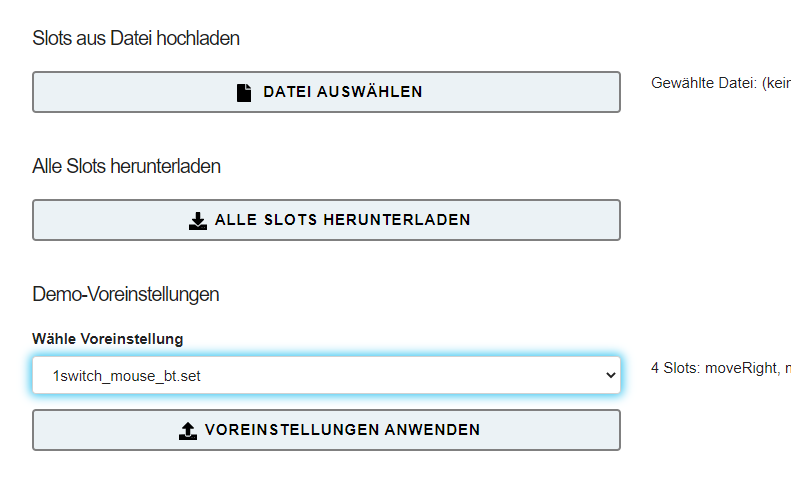
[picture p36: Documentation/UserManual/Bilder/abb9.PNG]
Abbildung10


*Abbildung 10*: Laden und Speichern von Konfigurationseinstellungen

### Einstellmöglichkeiten im Reiter „TIMINGS“

Über den Reiter **TIMINGS** können weitere Parameter für den Betrieb des FABI Systems eingestellt werden. In den Antitremor-Einstellungen können Schwellenwerte für Drücken und Loslassen bestimmt werden. Diese Antitremor Einstellungen dienen dazu, um versehentliches Drücken oder Loslassen durch Zittern der Hand zu vermeiden. Weiters können noch Schwellenwerte für langes Drücken, für Slot-Weiterschalten durch doppeltes Drücken und für den automatischen Linksklick bestimmt werden. All diese Einstellungen werden untenstehend näher erklärt.
**Hinweis**: diese Einstellungen beziehen sich nur auf den aktiven Slot (Speicherplatz).

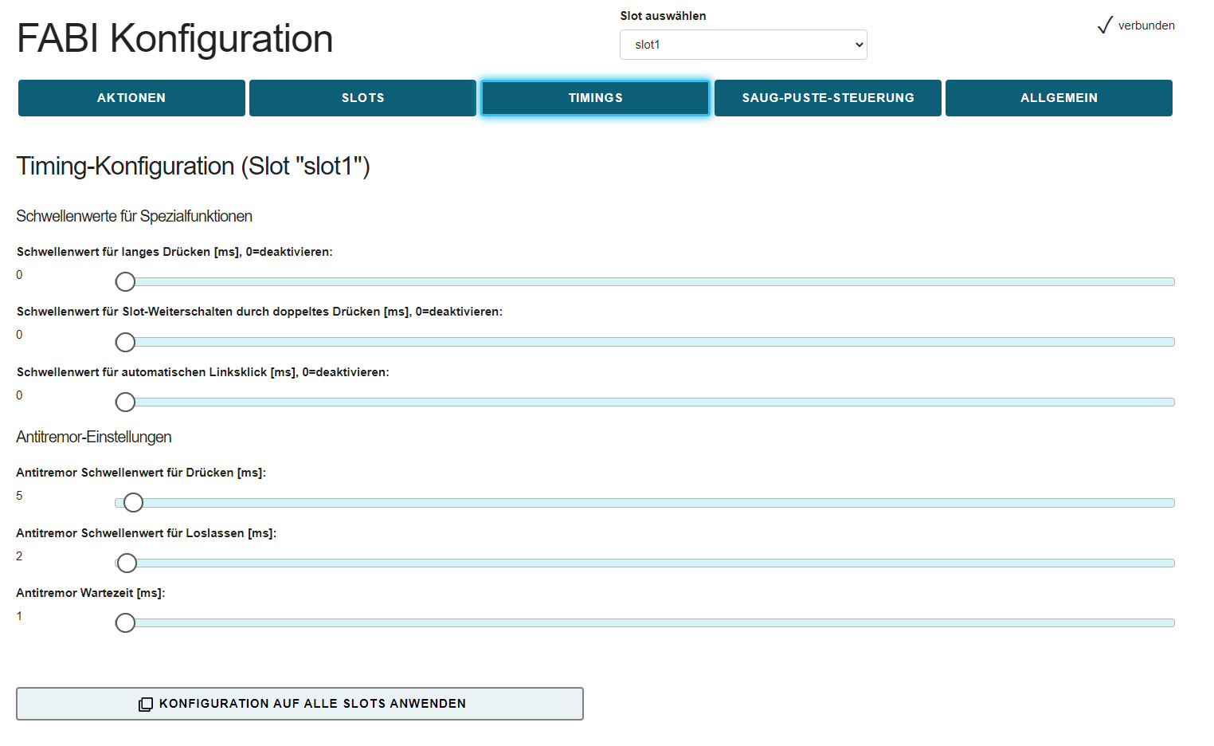
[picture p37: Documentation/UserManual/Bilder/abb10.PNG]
Abbildung11
 

*Abbildung 11*: Screenshot der weiteren Einstellungen im Reiter "Timings"

#### Antitremor-Einstellungen

Durch die Anti-Tremor Parameter können unterschiedliche Zeitspannen festgelegt werden, die beim Auslösen eines Tasters vom FABI-System überprüft werden. So kann das unwillkürliche Auslösen von Tasten bei Tremor oder Problemen der Feinmotorik minimiert werden:

* „Antitremor Schwellenwert für Drücken“ legt die minimale Zeitspanne fest, die ein Taster gedrückt werden muss, damit die Aktion durchgeführt wird. 
* „Antitremor Schwellenwert für Loslassen“ legt die minimale Zeitspanne fest, die ein Taster ausgelassen werden muss, damit das Auslassen erkannt wird.
* „Antitremor Wartezeit“ legt die minimale Zeitspanne fest, die zwischen hintereinander folgende Betätigungen eines Tasters vergehen muss.

#### Schwellenwerte für Spezialfunktionen

##### Schwellenwert für langes Drücken:

Der Schwellwert „**Schwellenwert für langes Drücken**“ legt eine Zeitspanne in Millisekunden fest, ab der das Drücken eines Tasters als „Langes Drücken“ interpretiert wird und folglich eine alternative Aktion ausgeführt werden kann. Dies ist vor allem dann sinnvoll, wenn eine Person nur eine geringe Anzahl von Tastern verwenden kann. Mit einem langen Tastendruck kann dann eine alternative Funktion (z.B. das Umschalten der Konfiguration) durchgeführt werden. Die entsprechenden Funktionen können im Reiter „AKTIONEN“ unter „Button x lange drücken“ definiert werden kann.
Die Lange-Drücken-Funktion ist deaktiviert, wenn eine Zeitspanne von 0 Millisekunden eingestellt ist.
Derzeit unterstützen nur Tasten, die bei den Anschlüssen 1, 2 oder 3 angesteckt werden, die Lange-Drücken Funktion. 

##### Verwendung der "Doppeltes Drücken" Funktion

Der Wert "**Schwellenwert für Slot-Weiterschalten durch doppeltes Drücken**" definiert die maximale Dauer eines "doppelten Tastendrucks" in Millisekunden. Wird ein schnelles zweimaliges Drücken einer Taste erkannt, erfolgt ein **automatischer Slotwechsel zum nächsten Slot**. Dies ist besonders dann sinnvoll, wenn eine Person nur eine einzige Taste benutzen kann: Durch zwei schnelle Tastendrücke kann die Funktion der Taste geändert werden. So könnten zum Beispiel mehrere Tastaturtasten abwechselnd gedrückt werden (z. B. zur Spielsteuerung) oder der Mauszeiger kann mit einem einzigen Schalter in verschiedene Richtungen bewegt werden.

##### Schwellenwert für automatischen Linksklick

Diese Einstellung ermöglicht es, einen linken Mausklick nach erfolgter Mausbewegung zu erzeugen. Verstreicht die gewählte Zeitspanne (in Millisekunden) ohne weitere Mausbewegungen, dann wird der Mausklick automatisch erzeugt. Dies erlaubt die vollständige Steuerung eines Mauszeigers mit einer geringen Anzahl von Tastern oder (in Kombination mit der automatischen Slotwechsel-Funktion) mit nur einem Taster. Ein Wert von 0 Millisekunden schaltet die automatische Klick-Funktion ab.

### Verwendung eines Drucksensors (Sip-/Puff) - (Reiter "SAUG-PUSTE-STEUERUNG")

Sofern ein analoger Drucksensor (optional!) mit dem FABI-System verbunden wird, können Aktionen für Sip und Puff (Ansaugen und Pusten) definiert werden. Der analoge Spannungswert wird dabei mit dem Lötkontakt A0 am Mikrocontroller Board verbunden. Weiters muss der Sensor mit Spannung versorgt werden (5V und GND richtig verbinden).

Daraufhin können im Reiter „**SAUG-PUSTE-STEUERUNG**“ entsprechende Schwellwerte für die Stärke des Ansaugens bzw. Hineinblasens eingestellt werden. Durch diese Aktivitäten können weitere Funktionen ausgelöst werden. Der Ruhewert des Sensors (wenn weder angesaugt noch gepustet wird) liegt in der Mitte des Wertebereiches, bei ca. 512.

Im Reiter „**AKTIONEN**“ kann, wie auch bei den Buttons, eine entsprechende Aktion ausgewählt werden, die beim Ansaugen bzw. beim Pusten ausgeführt werden soll.

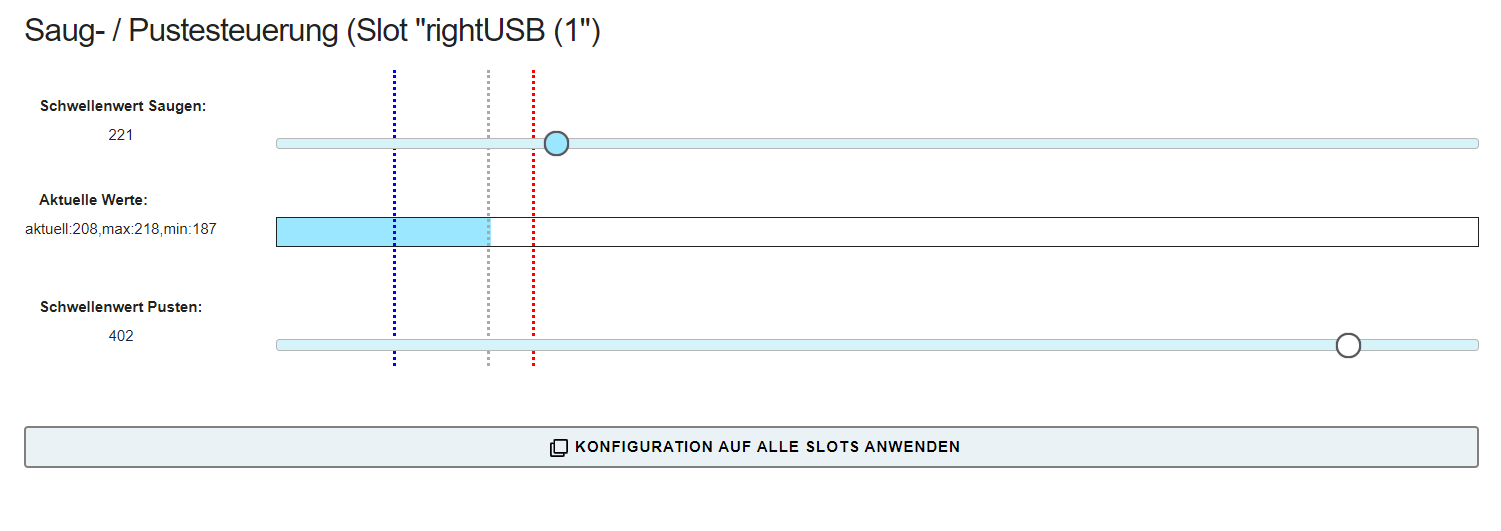
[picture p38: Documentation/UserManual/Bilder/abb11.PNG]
Abbildung12


*Abbildung 12*: Screenshot der Einstellungen für Saug- und Pusteschwellenwerte

### Einstellmöglichkeiten im Reiter „ALLGEMEIN“

Im Reiter **ALLGEMEIN** können die Bluetooth-Einstellungen angepasst werden, sowie die Firmware und die Bluetooth-Firmware überschrieben / aktualisiert werden.

TODO: beschreiben vom Testmodus

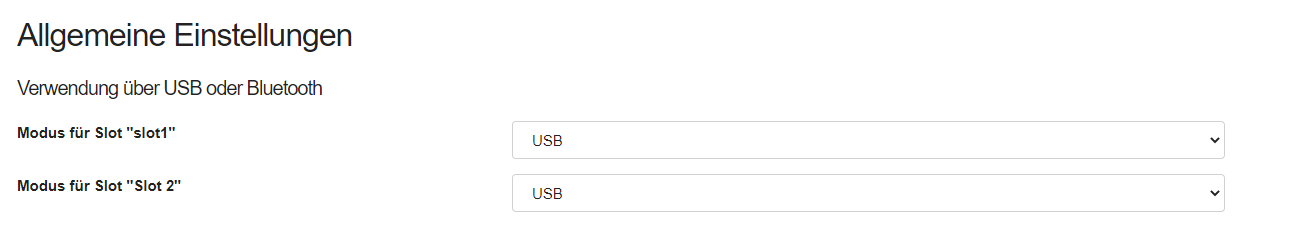
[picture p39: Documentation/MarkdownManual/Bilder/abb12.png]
Abbildung13
 

*Abbildung 13*: Screenshot der weiteren Einstellungen im Reiter "ALLGEMEIN"

#### Firmware überschreiben / aktualisieren

Durch Drücken dieses Buttons wird versucht, die aktuellste Software (Firmware) für FABI Hauptmodul (den Mikrocontroller) herunterzuladen und zu installieren. Dieser Vorgang kann einige Minuten dauern. Links neben dem Button werden die Versionsnummer der derzeit installierten Firmware und der für das Update verfügbaren Version dargestellt.  

#### Rücksetzen auf Defaulteinstellungen, Tastenkombinationen

Am unteren Ende des Reiters finden Sie den Button für das Zurücksetzen des FABI-Gerätes auf die Defaulteinstellungen. Dies ist sinnvoll, wenn die aktuellen Einstellungen Probleme mit der Verwendung der Gerätes verursachen. Weiters sehen Sie die Tastenkombinationen für das schnelle Wechseln zwischen den Reitern (Tabs).

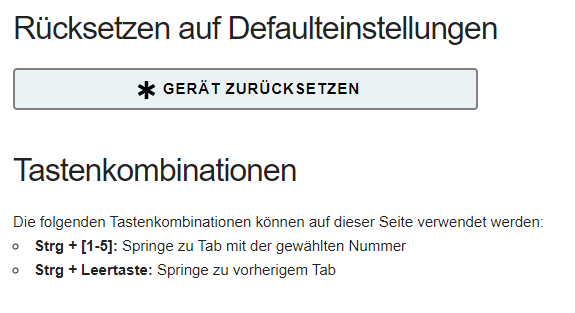
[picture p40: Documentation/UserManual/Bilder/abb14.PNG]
Abbildung14
 

*Abbildung 14*: Gerät zurücksetzen, Tastenkombinationen

**Viel Spaß beim Ausprobieren und beim Erstellen eigener FABI-Konfigurationen!**

### Liste der unterstützten Makrokommandos

| **Kürzel**  | **Funktion**                                                                                                                   | **Beispiel**                                                                                   |
| ----------- | ------------------------------------------------------------------------------------------------------------------------------ | ---------------------------------------------------------------------------------------------- |
| CL          | Klick linke Maustaste                                                                                                          |                                                                                                |
| CR          | Klick rechte Maustaste                                                                                                         |                                                                                                |
| CM          | Klick mittlere Maustaste (Zahnrad)                                                                                             |                                                                                                |
| CD          | Doppelklick linke Maustaste                                                                                                    |                                                                                                |
| HL          | Linke Maustaste halten                                                                                                         |                                                                                                |
| HR          | Rechte Maustaste halten                                                                                                        |                                                                                                |
| HM          | Mittlere Maustaste halten                                                                                                      |                                                                                                |
| TL          | Drücken oder Loslassen linke Maustaste (wechseln)                                                                              | Ändert: gedrückt <-> nicht gedrückt                                                            |
| TM          | Drücken oder Loslassen mittlere Maustaste (wechseln)                                                                           |                                                                                                |
| TR          | Drücken oder Loslassen rechte Maustaste (wechseln)                                                                             |                                                                                                |
| RL          | Linke Maustaste loslassen                                                                                                      |                                                                                                |
| RR          | Rechte Maustaste loslassen                                                                                                     |                                                                                                |
| RM          | Mittlere Maustaste loslassen                                                                                                   |                                                                                                |
| WU          | Nach unten scrollen                                                                                                            |                                                                                                |
| WD          | Nach oben scrollen                                                                                                             |                                                                                                |
| MX <int>    | Maus horizontal bewegen (x-Achse)                                                                                              | MX 4 -> bewegt Cursor 4 Pixel nach rechts                                                      |
| MY <int>    | Maus vertikal bewegen (y-Achse)                                                                                                | MY -10 -> bewegt Cursor 10 Pixel nach oben                                                     |
| KW <string> | keyboard write string: Schreibe Wort                                                                                           | KW Hallo! -> schreibt "Hallo!“ am Keyboard                                                     |
| KP <string> | key press:  Keyboard-Tasten drücken (und wieder loslassen). Tasten werden durch Tastenkürzel identifiziert (siehe Liste unten) | KP KEY_UP -> drückt die "Cursor-Up" Taste; KP KEY_CTRL KEY_ALT KEY_DELETE drückt alle 3 Tasten |
| KH <string> | key hold: Keyboard-Tasten drücken (und halten)                                                                                 | siehe KP                                                                                       |
| KT <string> | key toggle: Zustand der Keyboard-Tasten ändern (drücken wenn nicht gedrückt, loslassen wenn gedrückt)                          | siehe KP                                                                                       |
| KR <string> | key release: Spezifische Tasten auslassen; Tasten werden durch Tastenkürzel identifiziert (siehe Liste unten)                  | KR KEY_UP -> lässt die „Cursor-Up“ Taste los                                                   |
| RA          | release all = alle Tasten und Mausbuttons loslassen                                                                            |                                                                                                |
| WA <int>    | Warten (Millisekunden), bestimmte Anzahl Millisekunden warten                                                                  | WA 100 -> wartet 100 Millisekunden                                                             |
| NE          | next slot: nächsten Slot laden                                                                                                 |                                                                                                |
| LO <string> | load slot: Slot per Name laden; wechselt zum angegebenen Slot                                                                  | LO mouse                                                                                       |
| NC          | No command: keine Funktion                                                                                                     |                                                                                                |

### Liste der Kürzel für Keyboard-Tasten

| **Unterstützte Kürzel für Tastaturtasten**                                                                                                                                                                             |
| ---------------------------------------------------------------------------------------------------------------------------------------------------------------------------------------------------------------------- |
| **Buchstaben**                                                                                                                                                                                                         |
| KEY_A  KEY_B  KEY_C  KEY_D  KEY_E  KEY_F  KEY_G  KEY_H  <br/>KEY_I  KEY_J  KEY_K  KEY_L  KEY_M  KEY_N  KEY_O  KEY_P  <br/>KEY_Q  KEY_R  KEY_S  KEY_T  KEY_U  KEY_V  KEY_W  KEY_X KEY_Y KEY_Z                           |
| **Ziffern**                                                                                                                                                                                                            |
| KEY_1  KEY_2  KEY_3  KEY_4  KEY_5  KEY_6  KEY_7  KEY_8  KEY_9  KEY_0                                                                                                                                                   |
| **Funktionstasten**                                                                                                                                                                                                    |
| KEY_F1  KEY_F2  KEY_F3  KEY_F4  KEY_F5  KEY_F6  KEY_F7  KEY_F8  KEY_F9  KEY_F10  <br/>KEY_F11  KEY_F12  KEY_F13  KEY_F14  KEY_F15  KEY_F16  KEY_F17  KEY_F18  KEY_F19 <br/>KEY_F20  KEY_F21  KEY_F22  KEY_F23  KEY_F24 |
| **Navigationstasten**                                                                                                                                                                                                  |
| KEY_UP  KEY_DOWN  KEY_LEFT  KEY_RIGHT  KEY_TAB  KEY_PAGE_UP  KEY_PAGE_DOWN <br/>KEY_HOME  KEY_END                                                                                                                      |
| **Spezielle Tasten**                                                                                                                                                                                                   |
| KEY_ENTER  KEY_SPACE  KEY_BACKSPACE  KEY_DELETE  KEY_INSERT  KEY_ESC  KEY_NUM_LOCK<br/>KEY_SCROLL_LOCK  KEY_CAPS_LOCK  KEY_PAUSE<br/>                                                                                  |
| **Tasten für alternative Funktionen**                                                                                                                                                                                  |
| KEY_SHIFT  KEY_CTRL  KEY_ALT  KEY_RIGHT_ALT  KEY_GUI  KEY_RIGHT_GUI                                                                                                                                                    |

### Weiterführende Links und Software-Empfehlungen

Das FABI Button Interface eignet sich als alternatives Eingabesystem für verschiedenste Anwendungszwecke – von Computer/Smartphone-Kontrolle bis zu Verwendung von Spielen und Lernsoftware. Je nach Anzahl der verwendbaren Taster können hier auch Standard-Programme mit Maus / Keyboard ohne weitere Anpassung genutzt werden.

Falls die motorischen Fähigkeiten bzw. die Anzahl der verwendbaren Tasten-Funktionen sehr stark eingeschränkt sind, bieten speziell angepasste Applikationen auch Möglichkeiten für eine Verwendung mit nur einem Taster. Im folgenden werden einige interessante Ressourcen vorgestellt:

#### AsTeRICS und AsTeRICS Grid

Die weiteren Open Source Entwicklungen der [AsTeRICS Foundation](https://www.asterics-foundation.org) erlauben eine vielseitige Verwendung von Taster-Schnittstellen. Das [AsTeRICS](https://www.asterics.eu)-System ist ein Baukasten für Assistierende Technologien mit dem 1-Tasten Verfahren zur Computer-Kontrolle erstellt werden können. [AsTeRICS Grid](https://grid.asterics.eu) ist ein flexibles System für die Unterstütze Kommunikation (UK, AAC), das auch mit einzelnen Tastern verwendet werden kann.

#### SpecialEffect.org

Die gemeinnützige Organisation SpecialEffect ([www.specialeffect.org.uk](https://www.specialeffect.org.uk)) widmet sich der Verbreitung von barrierefreiem Spielen in Großbritannien und führt spezielle Anpassungen für Menschen mit Behinderung durch.

#### BLTT.org

Die Webseite Better Living Through Technology ([bltt.org/introduction-to-switch-access](https://bltt.org/introduction-to-switch-access)) bietet nützliche Informationen für Tasten-basierte Verwendung von Computern und Links zu vielen Software-Tools.

#### OneSwitch.org

Unter der Adresse [www.oneswitch.org.uk](https://www.oneswitch.org.uk/) hat Barrie Ellis eine Fülle von Tipps und Informationen für Single-Switch Gaming und spezielle Adaptierungen für Tasten-Steuerung von Computerspielen gesammelt. Besonders interessant sind die Spiele-Bibliothek, das One-Switch-Pulse System und die Verwendung von Spiele-Konsolen mittels Controller-Adaptern wie dem „Titan-Two“.

#### Click2Speak

[Click2Speak](https://www.click2speak.net) ist eine flexible Bildschirmtastatur (On-Screen Keyboard) für Windows, die zusätzliche nützliche Funktionen bietet- etwa eine Maus-Click-Auswahlbox.

## Kontaktinformationen

**AsTeRICS Foundation**

Webpage: <https://www.asterics-foundation.org>

Email: <office@asterics-foundation.org> 

## Haftungsausschluss

Die Fachhochschule Technikum Wien und die AsTeRICS Foundation übernehmen keinerlei Gewährleistung oder Haftung für die Funktionsfähigkeit der Hardware-/Softwaremodule oder die Richtigkeit der Dokumentation.

Weiters haften die FH Technikum Wien und die AsTeRICS Foundation nicht für etwaige Gesundheitsschäden durch eine Verwendung der bereitgestellten Hardware-/Softwaremodule. 
Die Verwendung der bereitgestellten Module und Informationen erfolgt auf eigenes Risiko!

## Danksagung

Wir danken Miriam Brenner, Fabian Schiegl und Fanny Peternell für ihre Unterstützung bei der Erstellung dieser Anleitung und Andreas Fußthaler für die Entwicklung der FABI-PCB-Version.

Dieses Projekt wurde von der Stadt Wien (Magistratsabteilung 23 für Wirtschaft, Arbeit und Statistik, MA 23) finanziell unterstützt (Projektnummer 14-02, 18-04).

Abbildung18

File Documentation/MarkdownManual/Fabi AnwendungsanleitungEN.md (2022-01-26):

FabiLogo

# FABI - User Manual

FabiFoto

____

# Welcome to FABI

FABI - the "Flexible Assistive Button Interface" - allows you to connect up to eight buttons to a computer or tablet/smartphone to trigger mouse or keyboard actions and perform other actions. A configured FABI module can be used with any computer (Windows, Linux or Mac), without installing special software, because when connected to the computer, the FABI module behaves like an ordinary computer mouse or keyboard. People for whom conventional input devices are not suitable can thus play computer games, surf the Internet, write e-mails and much more.

The FABI system can be used with commercially available switches, inexpensive arcade buttons, or even homemade electrical contacts. FABI consists of a hardware module (an inexpensive microcontroller that acts as a computer mouse or keyboard), other optional modules and sensors (Bluetooth add-on, sip/puff pressure sensor), and a graphical configuration interface for setting desired functions ("FABI configuration manager").

FABI is available as an open source kit (including corresponding assembly instructions for the hardware) and was developed as part of the AsTeRICS Academy project at the FH Technikum Wien. In 2017, the non-profit organization AsTeRICS Foundation was founded to further develop such technologies and systems and to make them available at low cost: [www.asterics-foundation.org](https://www.asterics-foundation.org/1270-2/).

All software modules, hardware design files, and how-to documents are available under free open source licenses and can be used and modified for free. We have made every effort to select the lowest cost components, yet not compromise on functionality and flexibility - making FABI an affordable pushbutton interface with extensive capabilities!

#### About this manual

This manual is used to explain the configuration interface and the possible settings and functions of the FABI system. The building instruction can be found in a separate document.

## Introduction

The FABI configuration manager is required to be able to define the functions of the buttons. Once a configuration has been saved in the FABI system, it remains there and the FABI system can be used to control different devices (e.g. Windows PC, Mac computer, tablet or smart phone with USB or Bluetooth connection). The configuration manager is only needed again if settings are changed.

The configuration manager has to be opened in the Chrome web browser and can be found at the following address: [fabi.asterics.eu](https://fabi.asterics.eu/index_fabi.htm). Below in figure 1 you can see the welcome page. If you click on CONNECT TO FABI CONNECTED VIA USB, no communication port (COM port) will be selectable in the selection box yet, unless you have connected the FABI module to the computer using the USB plug.

Abbildung1

*Figure 1*: Welcome page of the configuration manager

#### Connecting the USB micro cable

Abbildung2

*Figure 2*: Connecting the USB micro cable

#### Connecting the FABI device

To use the web configuration functions, follow the steps below. 1:

1. Make sure that the FABI device is connected to the computer.
2. After that, a communication port (COM port) with a certain number (e.g. COM4) should be selectable in a pop-up window. Click on this COM port and then click on *Connect*. (After unplugging the FABI module the COM port should disappear again).
3. **If you cannot see the user interface of the FABI configuration manager as in Figure 3, open the website again and select another COM port in the selection box that pops up. Then click again on *Connect*.**

## Using the configuration manager

After connecting to the communication port of the FABI system, you will now see the user interface of the FABI Configuration Manager (Figure 3).
Abbildung3 

*Figure 3*: FABI Configuration Manager User Interface

#### Port Status

The port status at the top right shows whether the FABI device is currently connected to the configuration manager. The set functions of the buttons can only be transferred to the device if "Connected" is displayed as the port status. If the device is no longer connected, you will return to the start page.

#### Save settings

The settings made are automatically saved and are immediately active in the FABI device. **The configurations are retained even if the FABI system is disconnected from the USB cable or power supply.**

### Using the memory locations (SLOTS tab)

Various function assignments of the buttons can be stored in up to 10 memory locations (***configuration slots***). These memory slots can also be changed during operation, e.g. via any button. As soon as the FABI device is supplied with power via the USB cable, the first memory location (slot) is automatically loaded and activated.

Abbildung4 

*Figure 4*: Creating, changing and deleting memory locations ("Slots").

A new memory slot is created in the **SLOTS** tab by clicking **CREATE SLOT**. The settings of the currently active slot are taken over (copied). With a preceding click in the text field, any name can be assigned to the new slot. In the top center there is a dropdown menu with the heading **"Select slot "**. If you click on the arrow on the right side of the text field, the dropdown menu opens showing slots that have already been saved and they can be selected here. In the **Slot configuration** list you can see all the available slots, with the active slot displayed in bold letters. Here you can also select the color, that is displayed when a slot is activated on the FABI device. The slots can be deleted individually or downloaded to the computer if required.

#### Selecting a color for the configuration

By clicking on the "Set color" field to the right of the corresponding slot in the **SLOTS** tab, a color selection dialog appears on the screen. A desired color can be selected here. The color light-emitting diode in the FABI housing assumes this color as soon as the corresponding configuration is activated. In this way, characteristic colors can be assigned to all configuration slots. **Note**: This function is only available in the new version (PCB version) of the FABI system.

#### Laden, Speichern und Übertragen von Konfigurationen

Wenn Sie im Reiter **SLOTS** weiter nach unten scrollen, finden Sie die Funktionen für das Slot-Backup. Hier Sie etwa Slots aus einer Datei hochladen: Dabei kann nach dem Anklicken von „Datei auswählen“ eine lokale Datei am Computer ausgewählt werden, die Konfigurationseinstellungen beinhaltet. Diese Einstellungen werden durch klicken von "Alle Slots hochladen und ersetzen" gesamt ins FABI-Gerät übertragen, dabei wird die aktuelle Konfiguration gelöscht. Es können jedoch auch einzelne Slots aus der Konfigurationsdatei zur aktiven FABI-Konfiguration hinzugefügt werden. Dafür werden nach dem Einblenden der erweiterten Optionen gewünschte Slots ausgewählt und durch klicken von "Gewählte(n) Slots hochladen" ins Gerät übertragen.

Das Speichern der aktuellen Konfigurationseinstellungen des FABI-Systems in eine Datei wird durch klicken von „Alle Slots herunterladen“ ermöglicht (siehe Abbildung 5). Hierbei wird die gesamte Konfiguration als Datei (.set) auf dem Computer gespeichert. Diese Einstellungsdatei kann anschließend auf dasselbe oder ein anderes FABI-Gerät übertragen werden. Dadurch können mehrere Setups (zum Beispiel für unterschiedliche AnwenderInnen oder Anwendungsfälle) auf einem Computer gespeichert werden und durch einen Klick aktiviert werden. 

**Achtung**: Beim Herunterladen einzelner Slots oder der gesamten Einstellungen werden die Dateien im Download-Verzeichnis des Web-Browsers abgelegt. Es ist sinnvoll, die Dateien anschließend in ein anderes Verzeichnis zu legen, damit sie leicht auffindbar sind und im Download-Verzeichnis nicht versehentlich gelöscht werden.

#### Demo-Voreinstellungen

Im Reiter **SLOTS** können ganz unten im Bereich "Demo-Voreinstellungen" (siehe Abbildung 5) vorbereitete Konfigurationseinstellungen ausgewählt werden. Diese bieten einen Überblick auf die Möglichkeiten des FABI-Systems und dienen als Anregung für eigene Anwendungen, etwa eine 1-Tasten-Maussteuerung, eine 2-Button-Steuerung von Computer und Smart-Phone oder eine Verwendung von Maus- und Cursortasten mit mehreren Buttons. Eine Beschreibung für die Demo-Konfigurationen kann angezeigt werden und bietet Kurzinformationen über die Funktionen bzw. Tastenbelegung.

Abbildung5 

*Abbildung 5*: Laden und Speichern von Konfigurationseinstellungen 

### Zuweisung der Taster-Funktionen (Reiter "AKTIONEN")

Im Reiter **AKTIONEN** können bis zu 8 Taster mit verschiedenen Funktionen belegt werden. Die Funktionen beinhalten etwa verschiedene Mausklicks, Mausbewegungen, Betätigung des Maus-Scrollrads oder von Keyboard-Tasten. Sie können die Aktion für den jeweiligen Taster ändern, indem Sie rechts vom gewünschten Button auf die unterstrichene (momentan aktive) Aktion klicken - siehe rotes Viereck in Abbildung 6. Dann erscheint ein Fenster, wo die gewünschte Aktions-Kategorie (hier: Maus) und die gewünschte Aktion ausgewählt werden kann (hier: Linke Maustaste halten). *Anmerkung:* Sollten mehr als 8 Taster benötigt werden, können mehrere FABI-Module parallel betrieben werden.

Abbildung6.1 

*Abbildung 6.1*: Aktion für Taster auswählen/ändern

Abbildung6.2 

*Abbildung 6.2*: Aktion für Taster auswählen (hier: Button 1)

#### Aktionskategorie Maus

##### Linke/Rechte/Mittlere Maustaste halten (für Dauer der Eingabe-Aktion)

Durch diese Funktionen bleibt die linke, rechte oder mittlere Maustaste gedrückt, solange der Taster gehalten wird (zum Beispiel, um eine Datei zu verschieben, ist es nötig, die linke Maustaste gedrückt zu halten). 

##### Klick linke/rechte/mittlere Maustaste

Mit diesen Funktionen kann einen Klick der linken, rechten oder mittleren Maustaste durch die Betätigung des Tasters ausgeführt werden. **Anmerkung**: ein Klick besteht aus drücken & loslassen der entsprechenden Maustaste, beides passiert kurz hintereinander nach der Betätigung des Buttons!

##### Doppelklick linke Maustaste

Ein Doppelklick der linken Maustaste ist zum Beispiel zum Öffnen einer Datei notwendig. Das Ausführen von schnellen Mausklicks kann jedoch für manche NutzerInnen schwierig sein. Durch das Zuweisen dieser Funktion kann ein Doppelklick durch einen einfachen Druck auf den Taster durchgeführt werden. 

##### Drücken oder Loslassen linke/rechte/mittlere Maustaste (wechseln)

Mit diesen Funktionen wird der Zustand der linken, rechten oder mittleren Maustaste geändert, wenn der Taster gedrückt wird. Beachten Sie, dass die Maustaste solange gedrückt bleibt, bis der Taster ein weiteres Mal gedrückt wird!

##### Nach unten / nach oben scrollen

Die Funktionen „Nach oben scrollen” und „nach unten scrollen” erzeugen durch den Taster Aktivitäten mit dem ein Scrollrad der Computermaus. Das Auslösen der “Nach oben scrollen” Funktion führt dazu, dass aufwärts gescrollt wird, bei der „Nach unten scrollen“ Funktion wird abwärts gescrollt (nützlich etwa zum Lesen von Dokumenten oder Webseiten).

##### Maus horizontal / vertikal bewegen – Mausbewegung in x- oder y-Richtung

Die „Maus horizontal bewegen (x-Achse)” und „Maus vertikal bewegen (y-Achse)” Funktionen erzeugen Computermausbewegungen entlang der gewählten Achsen. Für diese Funktionen können im darunter erscheinenden Feld Geschwindigkeitsparameter festgelegt werden. Beim Drücken des Tasters wird der Mauszeiger bis zu dieser maximalen Geschwindigkeit (zb. 20 oder -20) beschleunigt.

*Ein positiver Wert für die X-Richtung bewegt den Mauszeiger nach rechts.
Ein negativer Wert für die X-Richtung bewegt den Mauszeiger nach links.
Ein positiver Wert für die Y-Richtung bewegt den Mauszeiger nach unten.
Ein negativer Wert für die Y-Richtung bewegt den Mauszeiger nach oben.*

Abbildung7 

*Abbildung 7*: Screenshot der "Maus horizontal bewegen (x-Achse)"-Funktion bzw. Geschwindigkeitseinstellung

#### Aktionskategorie Tastatur

##### Taste(n) halten (für Dauer der Eingabe-Aktion)

Mit der Funktion "Taste(n) halten (für Dauer der Eingabe-Aktion)" können gewünschte Tasten der Computertastatur gehalten werden, sobald der Taster gedrückt wird. Die vorher ausgewählte Tastaturtaste(n) werden so lange gedrückt, wie der Taster gehalten wird. Die Tastenauswahl funktioniert wie bei dem Befehl "Tasten drücken" beschrieben.

##### Taste(n) drücken + wieder loslassen

Die „Taste(n) drücken + wieder loslassen ”-Funktion ermöglicht es, gewünschte Tasten (auch Kombinationen) des Computerkeyboards auszulösen, sobald der Taster gedrückt wird. Die Keyboard-Tasten werden gedrückt und sofort wieder losgelassen (also nicht so lange gehalten, wie der Taster gehalten bleibt). 

##### Taste(n) drücken oder auslassen (wechseln)

Mit der Funktion "Taste(n) drücken oder auslassen (wechseln)" können gewünschte Tasten auf der Computertastatur ihren Zustand ändern (also gedrückt werden bzw. losgelassen werden), sobald die Taste gedrückt wird. Beachten Sie, dass die Tastaturtaste solange gedrückt bleibt, bis die Taste ein weiteres Mal gedrückt wird! Die Tastenauswahl funktioniert wie bei dem Befehl "Tasten drücken" beschrieben.

Abbildung8 

*Abbildung 8*: Screenshot der "Press Key"-Funktion

Die gewünschte Taste kann jeweils aus der Auswahlbox gewählt werden, die rechts neben „Hinzufügen“ mit dem Pfeil aufklappbar ist. Danach klicken Sie auf „Hinzufügen“ und die Eingabe erscheint auch in der nächsten Zeile („Eingabe Tasten“). Das Beispiel in Abbildung 8 zeigt die Verwendung der Keyboard-Taste “KEY_E” – es wird dadurch bei jedem Druck des Tasters ein kleines „e“ geschrieben. Es ist möglich, auch mehrere Tasten für Tastenkombinationen auszuwählen, die dann gleichzeitig gedrückt/gehalten werden. Alternativ zur einzelnen Auswahl von Tasten aus der Auswahlbox können Tasten bzw. Tastenkombinationen auch automatisch erkannt werden, wenn das Feld "Tasten mit Tastatur eingeben" aktiviert wird. 
Bereits zugewiesene Tasten können durch klicken von „Löschen“ entfernt werden.

**Anmerkung:** Mit „KEY_SHIFT“ können Großbuchstaben verwendet werden. Alle weiteren unterstützen Keyboard-Tastenkürzel finden Sie im Anhang.

##### Schreibe Wort

Die „Write Text”-Funktion ermöglicht es, jedes Mal einen bestimmten Text zu schreiben, wenn der ausgewählte Taster gedrückt wird. Die kann z.B. für die Eingabe von Passwörtern nützlich sein. Wenn Sie „Schreibe Wort“ auswählen, scheint unter dem Dropdown-Menü ein leeres Textfeld auf, klicken Sie dann auf das Textfeld und geben Sie den gewünschten Text ein:
Abbildung9 

*Abbildung 9*: Screenshot der "Schreibe Wort"-Funktion

#### Aktionskategorie Gerät

##### Keine Funktion

Wenn „Keine Funktion” im Funktionsmenü ausgewählt wird, dann wird der entsprechede Taster deaktiviert.

##### Nächsten Slot laden – zur nächsten Konfiguration wechseln

Sobald der Taster gedrückt wird, wird der nächste Speicherplatz (Slot) aktiviert. Dadurch können die einzelnen Slots über einen Taster nach der Reihe durchgeschalten werden. Nach der letzten Konfiguration wird automatisch die erste Konfiguration aktiviert. (Diese Aktion ist nur relevant, wenn Sie Konfigurationen in mehreren Speicherplätzen abgelegt haben.)

##### Slot per Name laden – zu Konfiguration mit bestimmtem Namen wechseln

Sobald der Taster gedrückt wird, wird die Konfiguration mit dem angegebenen Namen aktiviert. (Diese Aktion ist nur relevant, wenn Sie Konfigurationen in mehreren Speicherplätzen abgelegt haben.)

#### Aktionskategorie Makro

##### Benutzerdefiniertes Makro – Makrokommandos ausführen

Diese fortgeschrittene Funktion ermöglicht die Ausführung mehrerer Kommandos über entsprechende Kommando-Kürzel, was eine hohe Flexibilität ermöglicht. Die einzelnen Kommandos werden im Textfeld durch Strichpunkte getrennt eingetragen. Kommandokürzel können auch mittels „Befehl hinzufügen“ ausgesucht und dann mit „HINZUFÜGEN“ im Makro hinzugefügt werden. Werden mehrere Befehle hintereinander hinzugefügt, so werden die Strichpunkte automatisch eingetragen.
Beispiel: Das Makrokommando MX 10; WA 500; KP KEY_A; bewegt den Mauscursor 10 Punkte nach rechts, wartet dann 500 Millisekunden und drückt dann die Keyboardtaste „A“.
**Anmerkung**: Die möglichen Befehle, die hinzugefügt werden können, werden aufgelistet, sobald der Pfeil rechts gedrückt wird. Die möglichen Kommando- und Tastenkürzel können aber auch händisch in der Zeile „Makro“ eingegeben werden, und sind auch am Ende dieser Dokumentation zu finden.

### Verwendung eines Drucksensors (Sip-/Puff) - (Reiter "SAUG-PUSTE-STEUERUNG")

Sofern ein analoger Drucksensor wie z.B. der Sensortyp MPXV7007GP mit dem FABI-System verbunden wird, können Aktionen für Sip und Puff (Ansaugen und Pusten) definiert werden. Der analoge Spannungswert wird dabei mit dem Lötkontakt A0 am Mikrocontroller Board verbunden. Weiters muss der Sensor mit Spannung versorgt werden (5V und GND richtig verbinden).

Daraufhin können im Reiter „**SAUG-PUSTE-STEUERUNG**“ entsprechende Schwellwerte für die Stärke des Ansaugens bzw. Hineinblasens eingestellt werden. Durch diese Aktivitäten können weitere Funktionen ausgelöst werden. Der Ruhewert des Sensors (wenn weder angesaugt noch gepustet wird) liegt in der Mitte des Wertebereiches, bei ca. 512.

Im Reiter „**AKTIONEN**“ kann, wie auch bei den Buttons, eine entsprechende Aktion ausgewählt werden, die beim Ansaugen bzw. beim Pusten ausgeführt werden soll.

Abbildung10 

*Abbildung 10*: Screenshot der Einstellungen für Saug- und Pusteschwellenwerte

### Einstellmöglichkeiten im Reiter „TIMINGS“

Über den Reiter **TIMINGS** können weitere Parameter für den Betrieb des FABI Systems eingestellt werden. In den Antitremor-Einstellungen können Schwellenwerte für Drücken und Loslassen bestimmt werden. Diese Antitremor Einstellungen dienen dazu, um versehentliches Drücken oder Loslassen durch Zittern der Hand zu vermeiden. Weiters können noch Schwellenwerte für langes Drücken, für Slot-Weiterschalten durch doppeltes Drücken und für den automatischen Linksklick bestimmt werden. All diese Einstellungen werden untenstehend näher erklärt.
**Hinweis**: diese Einstellungen beziehen sich nur auf den aktiven Slot (Speicherplatz).

Abbildung11 

*Abbildung 11*: Screenshot der weiteren Einstellungen im Reiter "Timings"

#### Antitremor-Einstellungen

Durch die Anti-Tremor Parameter können unterschiedliche Zeitspannen festgelegt werden, die beim Auslösen eines Tasters vom FABI-System überprüft werden. So kann das unwillkürliche Auslösen von Tasten bei Tremor oder Problemen der Feinmotorik minimiert werden:

* „Antitremor Schwellenwert für Drücken“ legt die minimale Zeitspanne fest, die ein Taster gedrückt werden muss, damit die Aktion durchgeführt wird. 
* „Antitremor Schwellenwert für Loslassen“ legt die minimale Zeitspanne fest, die ein Taster ausgelassen werden muss, damit das Auslassen erkannt wird.
* „Antitremor Wartezeit“ legt die minimale Zeitspanne fest, die zwischen hintereinander folgende Betätigungen eines Tasters vergehen muss.

#### Schwellenwerte für Spezialfunktionen

##### Schwellenwert für langes Drücken:

Der Schwellwert „**Schwellenwert für langes Drücken**“ legt eine Zeitspanne in Millisekunden fest, ab der das Drücken eines Tasters als „Langes Drücken“ interpretiert wird und folglich eine alternative Aktion ausgeführt werden kann. Dies ist vor allem dann sinnvoll, wenn eine Person nur eine geringe Anzahl von Tastern verwenden kann. Mit einem langen Tastendruck kann dann eine alternative Funktion (z.B. das Umschalten der Konfiguration) durchgeführt werden. Die entsprechenden Funktionen können im Reiter „AKTIONEN“ unter „Button x lange drücken“ definiert werden kann.
Die Lange-Drücken-Funktion ist deaktiviert, wenn eine Zeitspanne von 0 Millisekunden eingestellt ist.
Derzeit unterstützen nur Tasten, die bei den Anschlüssen 1, 2 oder 3 angesteckt werden, die Lange-Drücken Funktion. 

##### Verwendung der "Doppeltes Drücken" Funktion

Der Wert "**Schwellenwert für Slot-Weiterschalten durch doppeltes Drücken**" definiert die maximale Dauer eines "doppelten Tastendrucks" in Millisekunden. Wird ein schnelles zweimaliges Drücken einer Taste erkannt, erfolgt ein **automatischer Slotwechsel zum nächsten Slot**. Dies ist besonders dann sinnvoll, wenn eine Person nur eine einzige Taste benutzen kann: Durch zwei schnelle Tastendrücke kann die Funktion der Taste geändert werden. So könnten zum Beispiel mehrere Tastaturtasten abwechselnd gedrückt werden (z. B. zur Spielsteuerung) oder der Mauszeiger kann mit einem einzigen Schalter in verschiedene Richtungen bewegt werden.

##### Schwellenwert für automatischen Linksklick

Diese Einstellung ermöglicht es, einen linken Mausklick nach erfolgter Mausbewegung zu erzeugen. Verstreicht die gewählte Zeitspanne (in Millisekunden) ohne weitere Mausbewegungen, dann wird der Mausklick automatisch erzeugt. Dies erlaubt die vollständige Steuerung eines Mauszeigers mit einer geringen Anzahl von Tastern oder (in Kombination mit der automatischen Slotwechsel-Funktion) mit nur einem Taster. Ein Wert von 0 Millisekunden schaltet die automatische Klick-Funktion ab.

### Einstellmöglichkeiten im Reiter „ALLGEMEIN“

Im Reiter **ALLGEMEIN** können die Bluetooth-Einstellungen angepasst werden, sowie die Firmware und die Bluetooth-Firmware überschrieben / aktualisiert werden.

Abbildung12 

*Abbildung 12*: Screenshot der weiteren Einstellungen im Reiter "ALLGEMEIN"

#### USB Modus / Bluetooth Modus

Das optionale Bluetooth-Modul (Add-On) ermöglicht die Aussendung von Tastatur- und Maus-Aktionen zur einem verbundenen ("gepairten") bluetoothfähigen Gerät (etwa zu einem Smartphone oder Tablet-Computer). Ist ein Bluetooth-Modul im FABI-Gehäuse installiert, so kann in der Selektionsbox pro Slot definiert werden, ob die Maus- und Tastaturaktionen über USB oder über Bluetooth (oder über beides) erzeugt werden sollen (Abbildung 13):  

Abbildung13 

*Abbildung 13*: Bluetooth-Modus bzw. USB/Bluetooth Auswahl

**Hinweis**: Die Auswahl USB/Bluetooh-Modus ist nur sinnvoll, wenn das optionale Bluetooth-AddOn-Modul am FABI-Gerät angeschlossen ist (siehe “Verwendung des Bluetooth Moduls”). 
Da diese Einstellung pro Speicherplatz (Slot) definiert wird, kann sie für verschiedene Speicherplätze unterschiedlich sein. So kann mit demselben FABI-Gerät z.B. ein Laptop über USB und ein Smartphone/Tablet über Bluetooth angesteuert werden. Das Umschalten erfolgt einfach durch den Wechsel des aktiven Slots.

#### Firmware überschreiben / aktualisieren

Durch Drücken dieses Buttons wird versucht, die aktuellste Software (Firmware) für FABI Hauptmodul (den Mikrocontroller) herunterzuladen und zu installieren. Dieser Vorgang kann einige Minuten dauern. Links neben dem Button werden die Versionsnummer der derzeit installierten Firmware und der für das Update verfügbaren Version dargestellt.  

#### Bluetooth-Firmware überschreiben / aktualisieren

Durch Drücken dieses Buttons wird versucht, die aktuellste Software (Firmware) für das Bluetooth-Modul herunterzuladen und am Modul zu installieren. Dieser Vorgang kann einige Minuten dauern und ist nur dann möglich, wenn ein Bluetooth Modul mit dem FABI-System verbunden ist. Links neben dem Button werden die Versionsnummer der derzeit installierten Firmware und der für das Update verfügbaren Version dargestellt. Hier kann auch festgestellt werden, ob ein Bluetooth-Modul installiert ist bzw. ob das Modul erkannt wird.  

#### Rücksetzen auf Defaulteinstellungen, Tastenkombinationen

Am unteren Ende des Reiters finden Sie den Button für das Zurücksetzen des FABI-Gerätes auf die Defaulteinstellungen. Dies ist sinnvoll, wenn die aktuellen Einstellungen Probleme mit der Verwendung der Gerätes verursachen. Weiters sehen Sie die Tastenkombinationen für das schnelle Wechseln zwischen den Reitern (Tabs).

Abbildung14 

*Abbildung 14*: Gerät zurücksetzen, Tastenkombinationen

**Viel Spaß beim Ausprobieren und beim Erstellen eigener FABI-Konfigurationen!**

### Verwendung des Bluetooth Moduls

Das FABI System erlaubt die Verwendung eines optionalen Bluetooth “AddOn”-Moduls für drahtlose Geräteverbindungen zu Mobiltelefonen, Tablets und Computern mit Bluetooth-Funktion. Das Bluetooth-Modul ist seperat über die AsTeRICS Foundation erhältlich bzw. in der entsprechenden Version des FABI-Bausatzes enthalten. 

#### Installation des Bluetooth Moduls

Das Bluetooth Modul lässt sich sehr einfach mit der Platinen-Version des FABI-Systems (Bausatz) verwenden. (Eine Verwendung mit einem einzelnen Mikrocontroller ist auch möglich und wird in den weiterführenden Informationen im [Github Repository](https://github.com/asterics/esp32_mouse_keyboard) des Bluetooth Moduls genauer beschrieben.
Das Bluetooth Modul wird in der auf der Platine eingezeichneten Orientierung auf den 10-poligen Konnektor gesteckt. Öffnen Sie dafür das FABI-Gehäuse und drücken Sie den das Modul bis zum Anschlag auf die dafür vorgesehene Stiftleiste (siehe Abbildung 15):

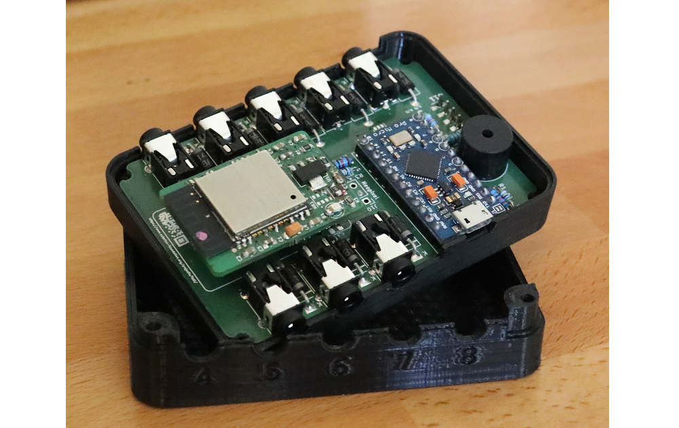
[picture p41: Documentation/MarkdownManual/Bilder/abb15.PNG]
Abbildung15
 

*Abbildung 15*: Bluetooth Modul, aufgesteckt auf die FABI-Platine

#### Verbinden mit einem Bluetooth-Gerät (pairing)

Das Bluetooth Modul zeigt durch schnelles Blinken (ca. 2 mal pro Sekunde) an, dass es bereit ist, mit einem Zielgerät eine Verbindung aufzunehmen. (Das Blinken des Moduls kann auf der Unterseite des FABI-Gehäuses wahrgenommen werden.) Das Zielgerät für die Verbindung (für das pairing) kann z.B. ein Mobiltelefon oder Tablet sein. In den Bluetooth-Einstellungen des Zielgerätes muss ein neues Gerät hinzugefügt werden. Hier sollte es möglich sein, das “FABI” Gerät auszuwählen. Bei erfolgreicher Verbindung sollte die Leuchtdiode des Bluetooth-Modules langsam blinken (ca. 1 Mal pro Sekunde). Das Zielgerät kann nun parallel zu dem über USB verbunden Gerät über das FABI System angesteuert werden. Die Entscheidung, ob eine Aktion über USB oder über  Bluetooth ausgeführt wird, erfolgt in den Einstellungen im Reiter **ALLGEMEIN** (siehe Abbildung 13).

### Liste der unterstützten Makrokommandos

| **Kürzel**  | **Funktion**                                                                                                                   | **Beispiel**                                                                                   |
| ----------- | ------------------------------------------------------------------------------------------------------------------------------ | ---------------------------------------------------------------------------------------------- |
| CL          | Klick linke Maustaste                                                                                                          |                                                                                                |
| CR          | Klick rechte Maustaste                                                                                                         |                                                                                                |
| CM          | Klick mittlere Maustaste (Zahnrad)                                                                                             |                                                                                                |
| CD          | Doppelklick linke Maustaste                                                                                                    |                                                                                                |
| HL          | Linke Maustaste halten                                                                                                         |                                                                                                |
| HR          | Rechte Maustaste halten                                                                                                        |                                                                                                |
| HM          | Mittlere Maustaste halten                                                                                                      |                                                                                                |
| TL          | Drücken oder Loslassen linke Maustaste (wechseln)                                                                              | Ändert: gedrückt <-> nicht gedrückt                                                            |
| TM          | Drücken oder Loslassen mittlere Maustaste (wechseln)                                                                           |                                                                                                |
| TR          | Drücken oder Loslassen rechte Maustaste (wechseln)                                                                             |                                                                                                |
| RL          | Linke Maustaste loslassen                                                                                                      |                                                                                                |
| RR          | Rechte Maustaste loslassen                                                                                                     |                                                                                                |
| RM          | Mittlere Maustaste loslassen                                                                                                   |                                                                                                |
| WU          | Nach unten scrollen                                                                                                            |                                                                                                |
| WD          | Nach oben scrollen                                                                                                             |                                                                                                |
| MX <int>    | Maus horizontal bewegen (x-Achse)                                                                                              | MX 4 -> bewegt Cursor 4 Pixel nach rechts                                                      |
| MY <int>    | Maus vertikal bewegen (y-Achse)                                                                                                | MY -10 -> bewegt Cursor 10 Pixel nach oben                                                     |
| KW <string> | keyboard write string: Schreibe Wort                                                                                           | KW Hallo! -> schreibt "Hallo!“ am Keyboard                                                     |
| KP <string> | key press:  Keyboard-Tasten drücken (und wieder loslassen). Tasten werden durch Tastenkürzel identifiziert (siehe Liste unten) | KP KEY_UP -> drückt die "Cursor-Up" Taste; KP KEY_CTRL KEY_ALT KEY_DELETE drückt alle 3 Tasten |
| KH <string> | key hold: Keyboard-Tasten drücken (und halten)                                                                                 | siehe KP                                                                                       |
| KT <string> | key toggle: Zustand der Keyboard-Tasten ändern (drücken wenn nicht gedrückt, loslassen wenn gedrückt)                          | siehe KP                                                                                       |
| KR <string> | key release: Spezifische Tasten auslassen; Tasten werden durch Tastenkürzel identifiziert (siehe Liste unten)                  | KR KEY_UP -> lässt die „Cursor-Up“ Taste los                                                   |
| RA          | release all = alle Tasten und Mausbuttons loslassen                                                                            |                                                                                                |
| WA <int>    | Warten (Millisekunden), bestimmte Anzahl Millisekunden warten                                                                  | WA 100 -> wartet 100 Millisekunden                                                             |
| NE          | next slot: nächsten Slot laden                                                                                                 |                                                                                                |
| LO <string> | load slot: Slot per Name laden; wechselt zum angegebenen Slot                                                                  | LO mouse                                                                                       |
| NC          | No command: keine Funktion                                                                                                     |                                                                                                |

### Liste der Kürzel für Keybord-Tasten

| **Unterstützte Kürzel für Tastaturtasten**                                                                                                                                                                             |
| ---------------------------------------------------------------------------------------------------------------------------------------------------------------------------------------------------------------------- |
| **Buchstaben**                                                                                                                                                                                                         |
| KEY_A  KEY_B  KEY_C  KEY_D  KEY_E  KEY_F  KEY_G  KEY_H  <br/>KEY_I  KEY_J  KEY_K  KEY_L  KEY_M  KEY_N  KEY_O  KEY_P  <br/>KEY_Q  KEY_R  KEY_S  KEY_T  KEY_U  KEY_V  KEY_W  KEY_X KEY_Y KEY_Z                           |
| **Ziffern**                                                                                                                                                                                                            |
| KEY_1  KEY_2  KEY_3  KEY_4  KEY_5  KEY_6  KEY_7  KEY_8  KEY_9  KEY_0                                                                                                                                                   |
| **Funktionstasten**                                                                                                                                                                                                    |
| KEY_F1  KEY_F2  KEY_F3  KEY_F4  KEY_F5  KEY_F6  KEY_F7  KEY_F8  KEY_F9  KEY_F10  <br/>KEY_F11  KEY_F12  KEY_F13  KEY_F14  KEY_F15  KEY_F16  KEY_F17  KEY_F18  KEY_F19 <br/>KEY_F20  KEY_F21  KEY_F22  KEY_F23  KEY_F24 |
| **Navigationstasten**                                                                                                                                                                                                  |
| KEY_UP  KEY_DOWN  KEY_LEFT  KEY_RIGHT  KEY_TAB  KEY_PAGE_UP  KEY_PAGE_DOWN <br/>KEY_HOME  KEY_END                                                                                                                      |
| **Spezielle Tasten**                                                                                                                                                                                                   |
| KEY_ENTER  KEY_SPACE  KEY_BACKSPACE  KEY_DELETE  KEY_INSERT  KEY_ESC  KEY_NUM_LOCK<br/>KEY_SCROLL_LOCK  KEY_CAPS_LOCK  KEY_PAUSE<br/>                                                                                  |
| **Tasten für alternative Funktionen**                                                                                                                                                                                  |
| KEY_SHIFT  KEY_CTRL  KEY_ALT  KEY_RIGHT_ALT  KEY_GUI  KEY_RIGHT_GUI                                                                                                                                                    |

### Weiterführende Links und Software-Empfehlungen

Das FABI Button Interface eignet sich als alternatives Eingabesystem für verschiedenste Anwendungszwecke – von Computer/Smartphone-Kontrolle bis zu Verwendung von Spielen und Lernsoftware. Je nach Anzahl der verwendbaren Taster können hier auch Standard-Programme mit Maus / Keyboard ohne weitere Anpassung genutzt werden.

Falls die motorischen Fähigkeiten bzw. die Anzahl der verwendbaren Tasten-Funktionen sehr stark eingeschränkt sind, bieten speziell angepasste Applikationen auch Möglichkeiten für eine Verwendung mit nur einem Taster. Im folgenden werden einige interessante Ressourcen vorgestellt:

#### AsTeRICS und AsTeRICS Grid

Die weiteren Open Source Entwicklungen der [AsTeRICS Foundation](https://www.asterics-foundation.org) erlauben eine vielseitige Verwendung von Taster-Schnittstellen. Das [AsTeRICS](https://www.asterics.eu)-System ist ein Baukasten für Assistierende Technologien mit dem 1-Tasten Verfahren zur Computer-Kontrolle erstellt werden können. [AsTeRICS Grid](https://grid.asterics.eu) ist ein flexibles System für die Unterstütze Kommunikation (UK, AAC), das auch mit einzelnen Tastern verwendet werden kann.

#### SpecialEffect.org

Die gemeinnützige Organisation SpecialEffect ([www.specialeffect.org.uk](https://www.specialeffect.org.uk)) widmet sich der Verbreitung von barrierefreiem Spielen in Großbritannien und führt spezielle Anpassungen für Menschen mit Behinderung durch.

#### BLTT.org

Die Webseite Better Living Through Technology ([bltt.org/introduction-to-switch-access](https://bltt.org/introduction-to-switch-access)) bietet nützliche Informationen für Tasten-basierte Verwendung von Computern und Links zu vielen Software-Tools.

#### OneSwitch.org

Unter der Adresse [www.oneswitch.org.uk](https://www.oneswitch.org.uk/) hat Barrie Ellis eine Fülle von Tipps und Informationen für Single-Switch Gaming und spezielle Adaptierungen für Tasten-Steuerung von Computerspielen gesammelt. Besonders interessant sind die Spiele-Bibliothek, das One-Switch-Pulse System und die Verwendung von Spiele-Konsolen mittels Controller-Adaptern wie dem „Titan-Two“.

#### Click2Speak

[Click2Speak](https://www.click2speak.net) ist eine flexible Bildschirmtastatur (On-Screen Keyboard) für Windows, die zusätzliche nützliche Funktionen bietet- etwa eine Maus-Click-Auswahlbox.

## Kontaktinformationen

**AsTeRICS Foundation**

Webpage: <https://www.asterics-foundation.org>
Email: <office@asterics-foundation.org> 

## Haftungsausschluss

Die Fachhochschule Technikum Wien und die AsTeRICS Foundation übernehmen keinerlei Gewährleistung oder Haftung für die Funktionsfähigkeit der Hardware-/Softwaremodule oder die Richtigkeit der Dokumentation.

Weiters haften die FH Technikum Wien und die AsTeRICS Foundation nicht für etwaige Gesundheitsschäden durch eine Verwendung der bereitgestellten Hardware-/Softwaremodule. 
Die Verwendung der bereitgestellten Module und Informationen erfolgt auf eigenes Risiko!

## Danksagung

Wir danken Miriam Brenner, Fabian Schiegl und Fanny Peternell für ihre Unterstützung bei der Erstellung dieser Anleitung und Andreas Fußthaler für die Entwicklung der FABI-PCB-Version.

Dieses Projekt wurde von der Stadt Wien (Magistratsabteilung 23 für Wirtschaft, Arbeit und Statistik, MA 23) finanziell unterstützt (Projektnummer 14-02, 18-04).

Abbildung18

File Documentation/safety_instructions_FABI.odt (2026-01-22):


Safety Instructions


Read this safety instructions carefully before using the FABI. Improper use might cause harm and injuries for which the AsTeRICS Foundation cannot be held responsible!

- Attach only appropriate buttons to this device. In case of doubt consult an expert.
- Do not use the device in combination with safety critical devices or other medical devices.
- Use the device only with non-critical consumer electronics.
- Do not use the device in an explosive environment.

FABI – EN safety instructions v1.1 – office@asterics-foundation.org

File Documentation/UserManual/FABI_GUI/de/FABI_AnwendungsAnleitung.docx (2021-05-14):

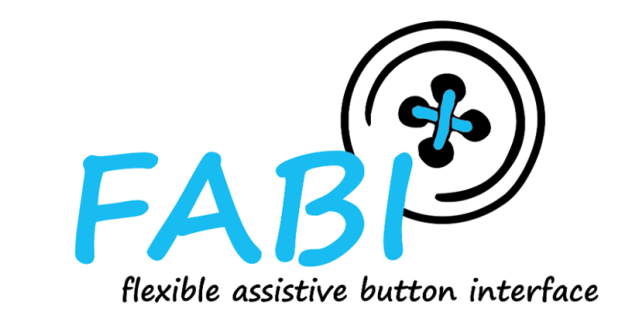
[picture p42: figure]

# FABI – Flexible Assistive Button Interface

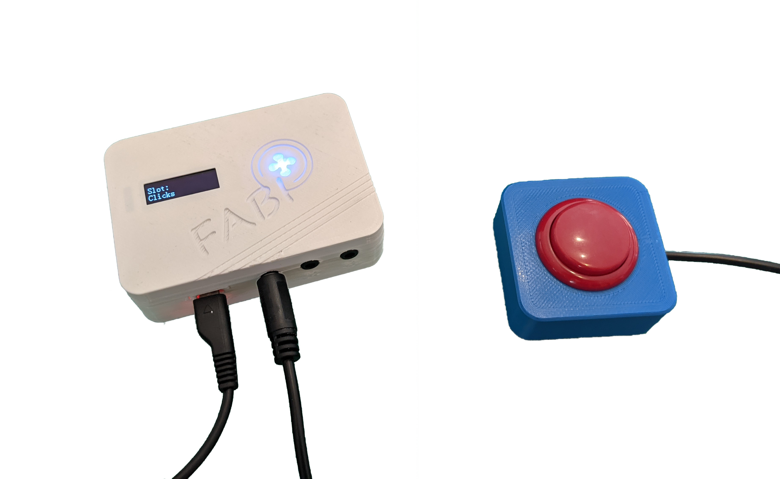
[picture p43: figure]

# Anwendungsanleitung

AsTeRICS Foundation

# Inhaltsverzeichnis

# Willkommen bei FABI

FABI - das „Flexible Assistive Button Interface“ - ermöglicht es, mehrere Taster (Buttons) an einen Computer oder ein Tablet/Smartphone anzuschließen und dadurch Maus- oder Keyboard-Aktionen auszulösen sowie andere Aktionen auszuführen. Ein konfiguriertes FABI-Modul kann mit jedem Computer (Windows, Linux oder Mac), ohne Installation von spezieller Software verwendet werden, weil sich das FABI-Modul beim Anschließen an den Computer wie eine gewöhnliche Computermaus bzw. eine Tastatur verhält. Menschen, für die herkömmliche Eingabegeräte nicht geeignet sind, können dadurch Computerspiele spielen, im Internet surfen, E-Mails schreiben und vieles mehr.

Das FABI Interface kann mit Buttons, Schaltern oder selbstgebauten elektrischen Kontakten verwendet werden. FABI besteht aus einem Hardware-Modul (einem kostengünstigen Mikrocontroller, der als Computermaus oder Tastatur fungiert) und einer grafischen Konfigurationsoberfläche („FABI-GUI“) zum Einstellen von gewünschten Funktionen.

FABI ist als Open Source Bausatz (inkl. entsprechender Bauanleitung für die Hardware) verfügbar und wurde im Rahmen des AsTeRICS Academy Projektes der FH Technikum Wien entwickelt. 2017 wurde die gemeinnützige Organisation AsTeRICS Foundation gegründet, um die derartige Technologien und Systeme weiterzuentwickeln und zur Verfügung stellen zu können: www.asterics-foundation.org.

Alle Softwaremodule, die Hardware Designdateien und die Dokumente für die Anleitungen sind unter freien Open Source Lizenzen verfügbar und können kostenlos verwendet und verändert werden. Wir haben uns bemüht, die kostengünstigsten Komponenten für die gewünschten Funktionen auszuwählen – was FABI zu der preisgünstigsten Tasterschnittstelle im derzeit bekannten Universum macht!

### Über diese Anleitung

Diese Anleitung dient zur Erklärung der Konfigurationsoberfläche und der möglichen Einstellungen und Funktionen. Die Bauanleitung ist in einem separaten Dokument zu finden.

Für das Einstellen von gewünschten Funktionen durch das FABI-GUI ist es unter Umständen notwendig, einen Treiber zu installieren (die Treiberinstallation wird in dieser Anleitung erklärt).

## Einleitung

Die Konfigurationssoftware „FABI-GUI“ wird benötigt, um die Funktionen der Taster / Buttons festlegen zu können. Nachdem eine Konfiguration im FABI-System gespeichert wurde, bleibt sie dort erhalten und das FABI-System kann zur Steuerung unterschiedlicher Geräte verwendet werden (z.B. Windows-PC, Mac-Computer, Tablet oder Smart-Phone mit USB-Anschluss.)
Die Konfigurationssoftware wird erst wieder benötigt, wenn Einstellungen geändert werden sollen.

### Herunterladen und Installieren der Software

Die ausführbare Datei FabiGUI.exe kann vom AsTeRICS GitHub-Verzeichnis heruntergeladen werden: https://github.com/asterics/FABI/releases/latest

Speichern Sie diese Datei in einem gewünschten Verzeichnis auf einem Windows PC oder Laptop.

Prinzipiell kann die FABI-GUI Software auch unter macOS oder Linux gestartet werden, mit Hilfe der „mono“ Software, die hier zu finden ist: https://www.mono-project.com/download/stable

Nachdem die FabiGUI.exe Datei von der oben genannten Quelle heruntergeladen wurde, starten Sie die Anwendung durch Doppelklick. Falls eine Error-Nachricht erscheint, ist vermutlich das „Microsoft.Net Framework“ auf Ihrem Computer nicht installiert. Laden Sie in diesem Fall das Framework von der folgenden Webseite herunter:
http://www.microsoft.com/en-us/download/confirmation.aspx?id=17718

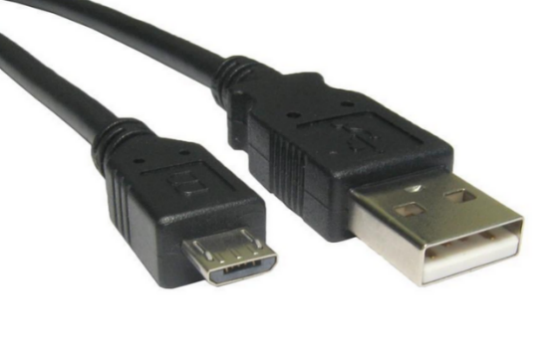
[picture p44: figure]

### Verbinden des USB-Micro Kabels

USB-Stecker mit dem Computer verbinden. Smartphones/Tablets können über einen
USB-OTG Adapter verbunden werden.

Verbinden Sie dieses Ende mit dem FABI Modul.

Vorsicht beim Einstecken, die Buchse am Mikro-controller sind nicht sehr stabil.

Falls Sie Probleme oder

Danach sollte in der FabiGUI-Software in der Auswahlbox „FABI Port“ ein Kommunikations-Anschluss (COM Port) mit bestimmter Nummer (z.B. COM4) auswählbar sein, siehe Abbildung 1. Nach dem Ausstecken des FABI-Moduls sollte der COM Port wieder verschwinden. Sollte kein neuer COM Port durch das Anstecken des FABI-Moduls erzeugt werden, installieren Sie bitte die Arduino Software von folgender Quelle und versuchen Sie es dann erneut: https://www.arduino.cc/en/software

Bei Fragen zum Download oder Problemen bei der Installation der Software schreiben Sie uns bitte eine E-Mail an: office@asterics-foundation.org

## Verwendung der FABI-GUI Anwendung

Nachdem die FabiGUI.exe Anwendung gestartet wurde, sollte sich das folgende Fenster öffnen:

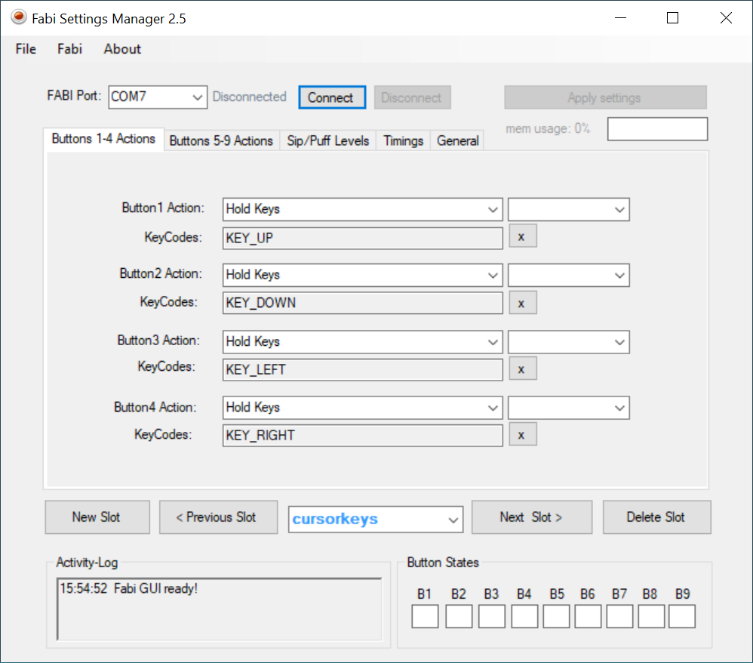
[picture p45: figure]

Abbildung 1: FabiGUI Benutzeroberfläche

#### Das FABI-Gerät verbinden:

Um die Funktionen der Konfigurationssoftware zu verwenden, folgen Sie den nachfolgenden Schritten:

1. Vergewissern Sie sich, dass das FABI- Gerät mit dem Computer verbunden ist.
2. Wählen Sie einen COM-Port und klicken Sie auf den „Connect”-Button auf der rechten Seite der Auswahlbox. Sobald das Gerät erfolgreich verbunden wurde, erscheint ein Dialog am Bildschirm, der die Geräteversion anzeigt und es Ihnen ermöglicht, die aktuellen Einstellungen vom FABI-Gerät zu laden. Wenn Sie dies möchten, klicken Sie „Ja“ - ansonsten bleiben die vorgeschlagenen Standardeinstellungen erhalten (siehe Abbildung 2).
3. Sollte der Dialog nicht angezeigt werden, wählen Sie bitte einen anderen COM-Port in der Auswahlbox und drücken erneut „Connect“.

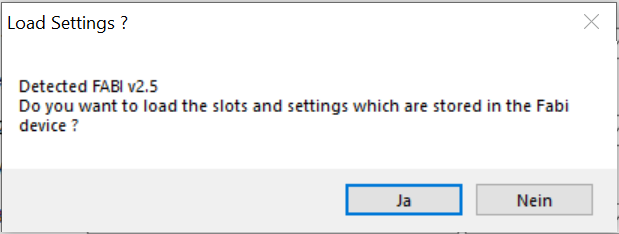
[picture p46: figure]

Abbildung 2: Das Programm wurde erfolgreich mit dem Port des Mikrokontrollers verbunden

#### Port Status

Der Portstatus neben der Auswahlbox für den FABI Port (links oben) zeigt an, ob das Gerät aktuell mit der Anwendung verbunden ist oder nicht. Die eingestellten Funktionen der Taster können nur dann ins Gerät übertragen werden, wenn als Port Status „Connected” angezeigt wird.

#### Activity Log

Der Bereich Activity Log wird im unteren Bereich des Anwendungsfensters angezeigt und stellt die aktuellen Fehler- und Statusmeldungen der Anwendung dar.

#### Einstellungen speichern (Apply Settings)

Um die Änderungen dauerhaft in einem verbundenen FABI-Gerät zu speichern, können Sie jederzeit den Button „Apply settings“ drücken. Sobald Einstellungen gespeichert oder aktiviert werden, erhalten Sie eine Nachricht im Activity Log.

#### Verwendung der Speicherplätze (Slots)

Funktionseinstellungen können in bis zu 10 Speicherplätze (Konfigurations-Slots) abgelegt werden. Diese Speicherplätze können auch während des Betriebes gewechselt werden (z.B. über einen bestimmten Taster). Die Konfigurationen bleiben erhalten, wenn der Mikrocontroller vom USB-Kabel / von der Stromversorgung getrennt wird. Sobald das FABI-Gerät über das USB Kabel wieder mit Strom versorgt wird, wird der erste Slot automatisch geladen und verwendet.

Ein neuer Speicherplatz wird durch Klicken von „New Slot“ angelegt. Mit einem anschließenden Klick in das Textfeld kann ein beliebiger Name vergeben werden. Wenn Sie auf der rechten Seite des Textfeldes auf den Pfeil klicken, öffnet sich ein Dropdown-Menu, das bereits gespeicherte Slots anzeigt und wo diese ausgewählt werden können. Durch Klicken von „Previous Slot“ oder „Next Slot“ kann schrittweise zwischen den existierenden Speicherplätzen gewechselt werden. Klicken Sie „Delete slot”, um den aktuellen Speicherplatz zu löschen.

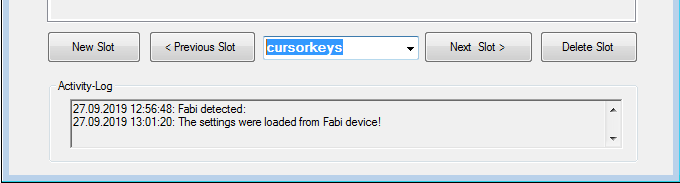
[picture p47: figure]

Abbildung 3: Anlegen, Wechseln und Löschen von Speicherplätzen (“Slots“)

Bitte beachten: Änderungen werden immer im aktuell angezeigten Speicherplatz (Konfigurations-Slot) durchgeführt. Änderungen werden aber erst dann ins Gerät übertragen, sobald „Apply Settings“ gedrückt wird!

#### Laden, Speichern und Übertragen von Konfigurationen

Das File-Menü ermöglicht es, die gesamte Konfiguration als Datei (.set) auf dem Computer zu speichern. Diese Einstellungsdatei kann dann auf dasselbe oder ein anderes FABI-Gerät übertragen werden. Dadurch können mehrere Setups (zum Beispiel für unterschiedliche AnwenderInnen oder Anwendungsfälle) auf einem Computer gespeichert werden und durch einen Klick aktiviert werden. Ein Datenauswahl-Fenster ermöglicht die Auswahl eines gewünschten Dateinamens zum Speichern (Save Settings) oder Laden (Load Settings) von Konfigurationseinstellungen.

Achtung: Beim Übertragen der Einstellungen von einer gespeicherten Datei auf das FABI-Gerät werden die aktuellen Konfigurationseinstellungen überschrieben.

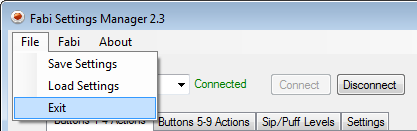
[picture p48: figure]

Abbildung 4: Laden und Speichern von Konfigurationseinstellungen

## Zuweisung der Taster-Funktionen

Durch die FabiGUI Anwendungen können bis zu 9 Taster mit verschiedenen Funktionen, belegt werden. Solche Funktionen beinhalten etwa verschiedene Mausklicks, Mausbewegungen, scrollen oder Keyboard-Tasten drücken.

Bitte beachten Sie, dass beim 3D-gedruckten FABI Gehäuse lediglich 8 der 9 möglichen Taster auch Ausnehmungen für die Anschlüsse (Klinkenbuchsen) haben. Meist werden allerdings ohnehin weniger Taster verwendet. Sollten mehr als 8 Taster benötigt werden, können mehrere FABI-Module parallel betrieben werden.

Im folgenden Kapitel wird die Auswahl der Funktionen für die Taster erklärt.

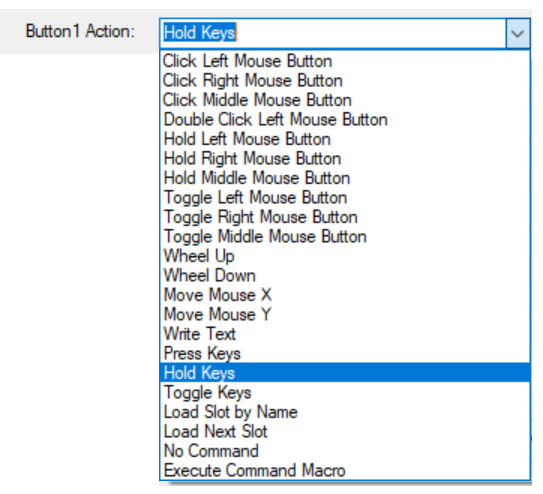
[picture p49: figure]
ScreenHunter 47

Abbildung 5: Auswahl möglicher Funktionen für Taster

#### Click Left / Right / Middle Mouse Button

Mit diesen Funktionen kann einen Klick der linken, rechten oder mittleren Maustaste durch die Betätigung des Tasters ausgeführt werden. Anmerkung: ein Click besteht aus drücken & loslassen der entsprechenden Maustaste, beides passiert kurz hintereinander nach der Betätigung des Buttons!

#### Double Click Left Mouse Button

Ein Doppelklick der linken Maustaste ist zum Beispiel zum Öffnen einer Datei notwendig. Das Ausführen von schnellen Mausklicks kann jedoch für manche NutzerInnen schwierig sein. Durch das Zuweisen der Funktion „Double Click Left Mouse Button“ kann ein Doppelklick durch einen einfachen Druck auf den Taster durchgeführt werden.

#### Hold Left / Right / Middle Mouse Button

Durch diese Funktionen bleibt die linke, rechte oder mittlere Maustaste gedrückt, solange der Taster gehalten wird (zum Beispiel, um eine Datei zu verschieben, ist es nötig, die linke Maustaste gedrückt zu halten).

#### Toggle Left / Right / Middle Mouse Button

Mit diesen Funktionen wird der Zustand der linken, rechten oder mittleren Maustaste geändert, wenn der Taster gedrückt wird. Beachten Sie, dass die Maustaste solange gedrückt bleibt, bis der Taster ein weiteres Mal gedrückt wird!

#### Wheel Up / down – Aufwärts/ abwärts scrollen

Die Funktionen „Wheel Up” und „Wheel down” erzeugen durch den Taster Aktivitäten mit dem ein Scrollrad der Computermaus. Das Auslösen der “Wheel Up” Funktion führt dazu, dass aufwärts gescrollt wird, bei der „Wheel down“ Funktion wird abwärts gescrollt (nützlich etwa zum Lesen von Dokumenten oder Webseiten).

#### Mouse Move X/Y – Mausbewegung in X- oder Y-Richtung

Die „Move Mouse X” und „Move Mouse Y” Funktionen erzeugen Computermausbewegungen entlang der gewählten Achsen. Für diese Funktionen können Geschwindigkeitsparameter festgelegt werden. Beim Drücken des Tasters wird der Mauszeiger bis zu dieser maximalen Geschwindigkeit beschleunigt.

Ein positiver Wert für die X-Richtung bewegt den Mauszeiget nach rechts.

Ein negativer Wert für die X-Richtung bewegt den Mauszeiget nach links.

Ein positiver Wert für die Y-Richtung bewegt den Mauszeiger nach unten.
Ein negativer Wert für die Y-Richtung bewegt den Mauszeiget nach oben.

Abbildung 6: Screenshot der "Mouse X"-Funktion bzw. Geschwindigkeitseinstellung

#### Write text – Text schreiben

Die „Write Text”-Funktion ermöglicht es, jedes Mal einen bestimmten Text zu schreiben, wenn ein der Taster gedrückt wird. Wenn Sie „Write Text“ auswählen, scheint unter dem Dropdown-Menü ein leeres Textfeld auf, klicken Sie dann auf das Textfeld und geben Sie den gewünschten Text ein:

Abbildung 7: Screenshot der „Write Text"-Funktion

#### Press Keys – Tastaturtasten drücken

Die „Press Keys”-Funktion ermöglicht es, gewünschte Tasten des Computerkeyboards auszulösen, sobald der Taster gedrückt wird. Die Keyboard-Tasten werden gedrückt und sofort wieder losgelassen (also nicht so lange gehalten, wie der Taster gehalten bleibt). Die gewünschte Taste kann in aus einer Auswahlbox gewählt werden, die links eingeblendet wird:

Abbildung 8: Screenshot der "Press Key"-Funktion

Das Beispiel (siehe Abbildung 8) zeigt die Verwendung der Keyboard-Taste “KEY_E” – es wird dadurch bei jedem Druck des Tasters ein kleines „e“ geschrieben.

Es ist möglich, auch mehrere Tasten für Tastenkombinationen auszuwählen, die dann gleichzeitig gedrückt/gehalten werden. Bereits zugewiesene Tasten können durch klicken von „X“ entfernt werden.

Anmerkung: Mit „KEY_SHIFT“ können Großbuchstaben verwendet werden. Alle weiteren unterstützen Keyboard-Tastenkürzel finden Sie im Anhang.

#### Hold Keys - Tastaturtasten halten

Mit der Funktion "Hold Keys" können gewünschte Tasten der Computertastatur gehalten werden, sobald die Taste gedrückt wird. Die Tastaturtasten werden so lange gedrückt, wie die Taste gehalten wird. Die Tastenauswahl funktioniert wie bei dem Befehl "Tasten drücken" beschrieben.

#### Toggle Keys – Zustand der Tastaturtasten ändern

Mit der Funktion "Toggle Keys" können gewünschte Tasten auf der Computertastatur ihren Zustand ändern, sobald die Taste gedrückt wird. Beachten Sie, dass die Tastaturtaste solange gedrückt bleibt, bis die Taste ein weiteres Mal gedrückt wird! Die Tastenauswahl funktioniert wie bei dem Befehl "Tasten drücken" beschrieben.

#### Load Slot by Name – zu Konfiguration mit bestimmtem Namen wechseln

Sobald der Taster gedrückt wird, wird die Konfiguration mit dem angegebenen Namen aktiviert. (Diese Aktion ist nur relevant, wenn Sie Konfigurationen in mehreren Speicherplätzen abgelegt haben.)

#### Load Next Slot – zur nächsten Konfiguration wechseln

Sobald der Taster gedrückt wird, wird die nächste Konfiguration (der nächste Speicherplatz) aktiviert. Nach der letzten Konfiguration wird automatisch die erste Konfiguration aktiviert. (Diese Aktion ist nur relevant, wenn Sie Konfigurationen in mehreren Speicherplätzen abgelegt haben.)

#### No Command – keine Aktion

Wenn „No Command” im Funktionsmenü ausgewählt wird, dann wird keine Aktion ausgeführt, wenn der Taster gedrückt wird.

#### Execute Command Macro – Makrokommandos ausführen

Diese Aktion ermöglicht die Ausführung mehrerer Kommandos über entsprechende Kommando-Kürzel, die im Textfeld durch Strichpunkte getrennt eingetragen.

Beispiel: Das Makrokommando MX 10; WA 500; KP KEY_A; bewegt den Mauscursor 10 Punkte nach rechts, wartet dann 500 Millisekunden und drückt dann die Keyboardtaste „A“.

Anmerkung: Eine Liste der möglichen Kommando- und Tastenkürzel ist im Anhang zu finden.

## Verwendung eines Drucksensors (Sip-/Puff)

Das FABI Gerät ermöglicht die Verwendung eines optionalen Drucksensors (Sip/Puff bzw. Saug-Blas-Sensor). Es können analoge Drucksensoren wie z.B. der Sensortyp MPXV7007GP (https://www.digikey.at/product-detail/de/nxp-usa-inc/MPXV7007GP/MPXV7007GP-ND/1168441) verwendet werden. Der analoge Spannungswert wird dabei mit dem Lötkontakt A0 am Mikrocontroller Board verbunden. Weiters muss der Sensor mit Spannung versorgt werden (5V und GND richtig verbinden.

Daraufhin können im Reiter „Sip/Puff Levels“ entsprechende Schwellwerte für die Stärke des Ansaugens bzw. Hineinblasens eingestellt werden. Durch diese Aktivitäten können weitere Funktionen ausgelöst werden. Der Ruhewert des Sensors (wenn weder angesaugt noch gepustet wird) liegt in der Mitte des Wertebereiches, bei ca. 512.

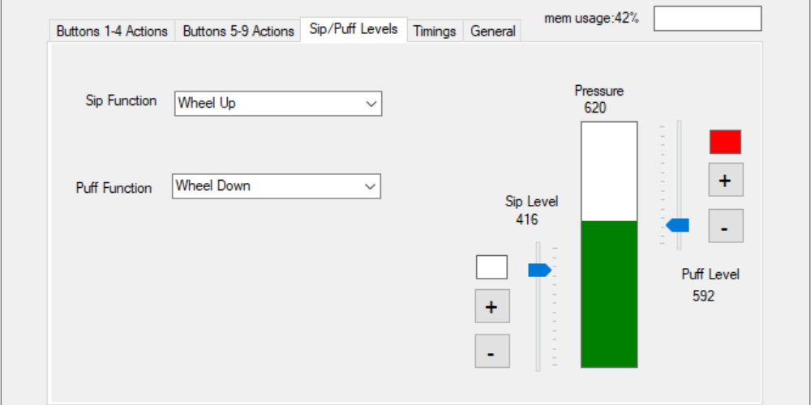
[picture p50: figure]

Abbildung 9: Screenshot der Einstellungen für Sip- und Puff

## Einstellmöglichkeiten im Timings - Tab

Über den Reiter „Timings“ können weitere Parameter für den Betrieb des FABI Systems eingestellt werden, darunter die Verwendung von „Long-Press“ -Funktionen wenn Taster besonders lang gedrückt werden, und die Einstellung von Anti-Tremor Filtern für minimale Zeitspannen beim Drücken von Tasten um versehentliches Drücken zu vermeiden – siehe Abbildung 10.
Hinweis: diese Einstellungen beziehen sich nur auf den aktiven Slot (Speicherplatz).


Abbildung 10: Screenshot der weiteren Einstellmöglichkeiten im Settings Menu

### Verwendung der „Anti-Tremor“ Funktionen

Durch die Anti-Tremor Parameter können unterschiedliche Zeitspannen festgelegt werden, die beim Auslösen eines Tasters vom FABI-System überprüft werden. So kann das unwillkürliche Auslösen von Tasten bei Tremor oder Problemen der Feinmotorik minimiert werden:

- „Antitremor Time for Press“ legt die minimale Zeitspanne fest, die ein Taster gedrückt werden muss, damit die Aktion durchgeführt wird.
- „Antitremor Time for Release“ legt die minimale Zeitspanne fest, die ein Taster ausgelassen werden muss, damit das Auslassen erkannt wird.
- „Antitremor Idle Time“ legt die minimale Zeitspanne fest, die zwischen hintereinander folgende Betätigungen eines Tasters vergehen muss.

### Verwendung der „Long Press“ Funktionen

Der Schwellwert „Threshold Time Short/Long Press“ legt eine Zeitspanne in Millisekunden fest, ab der das Drücken eines Tasters als „Long-Press“ interpretiert wird und folglich eine alternative Aktion ausgeführt werden kann. Dies ist vor allem dann sinnvoll, wenn eine Person nur eine geringe Anzahl von Tastern verwenden kann. Mit einem lagen Tastendruck kann dann eine alternative Funktion oder das Umschalten der Konfiguration durchgeführt werden.

Die Longpress-Funktion ist deaktiviert, wenn eine Zeitspanne von 0 Millisekunden eingestellt ist.

Derzeit unterstützen nur Tasten, die bei den Anschlüssen 1, 2 oder 3 angesteckt werden, die Long-Press Funktion. Da die Tasten 1,2 und 3 aber schon mit Funktionen für die normale (kurze) Betätigung belegt sind, müssen die gewünschten Funktionen für die „longpress“-Aktivität bei anderen Tastern eingetragen werden, die in der Anwendung ansonsten nicht in Verwendung sind:

Bitte beachten:

Wenn Button1 lang gedrückt wird, wird die Funktion ausgeführt, die für Button7 eingestellt wurde. Wenn Button2 lang gedrückt wird, wird die Funktion ausgeführt, die für Button8 eingestellt wurde. Wenn Button3 lang gedrückt wird, wird die Funktion ausgeführt, die für Button9 eingestellt wurde.

### Verwendung der "Double Press" Funktion

Der Wert "Time Threshold for Double Press" definiert die maximale Dauer eines "doppelten Tastendrucks" in Millisekunden. Wird ein schnelles zweimaliges Drücken einer Taste erkannt, erfolgt ein automatischer Slotwechsel zum nächsten Slot. Dies ist besonders dann sinnvoll, wenn eine Person nur eine einzige Taste benutzen kann: Durch zwei schnelle Tastendrücke kann die Funktion der Taste geändert werden. So könnten zum Beispiel mehrere Tastaturtasten abwechselnd gedrückt werden (z. B. zur Spielsteuerung) oder der Mauszeiger kann mit einem einzigen Schalter in verschiedene Richtungen bewegt werden.

## Einstellmöglichkeiten im General Tab

Im Bereich „General“ können die Bluetooth-Einstellungen und die automatische Verweilzeit angepasst werden.

Hinweis: diese Einstellungen beziehen sich nur auf den aktiven Slot (Speicherplatz).


Abbildung 11: Screenshot der weiteren Einstellmöglichkeiten im General Menu

### Select Slot Color – Auswahl einer Farbe für die Konfiguration

Durch das Anklicken des Farbfeldes erscheint ein Farbwahl-Dialog am Bildschirm. Hier kann eine gewünschte Farbe selektiert werden. Die Farb-Leichtdiode im FABI-Gehäuse nimmt immer diese Farbe an, sobald die aktuelle Konfiguration aktiviert wird. So lassen sich allen Konfigurations-Slots charakteristische Farben zuordnen. Hinweis: Diese Funktion ist nur in der PCB-Version des FABI-Systems verfügbar.

### Automatic Left Click – Automatisches Klicken nach Verweildauer

Diese Einstellung ermöglicht es, einen linken Mausklick nach erfolgter Mausbewegung zu erzeugen. Verstreicht die gewählte Zeitspanne (in Millisekunden) ohne weitere Mausbewegungen, dann wird der Mausklick automatisch erzeugt. Dies erlaubt die vollständige Steuerung eines Mauszeigers mit einer geringen Anzahl von Tastern oder (in Kombination mit der automatischen Slotwechsel-Funktion) mit nur einem Taster. Ein Wert von 0 Millisekunden schaltet die automatische Klick-Funktion ab.

### Bluetooth Modus

Die Auswahl dieser Selektionsbox definiert, ob die Maus- und Tastaturaktionen über USB oder über Bluetooth (oder über beides) erzeugt werden sollen:


Abbildung 12: Bluetooth Modus bzw. USB/Bluetooth Auswahl

Hinweis: Die Auswahl USB/Bluetooh-Modus ist nur sinnvoll, wenn das optionale Bluetooth-AddOn-Modul am FABI-Gerät angeschlossen ist (siehe “Verwendung des Bluetooth Moduls”).

Diese Einstellung wird pro Speicherplatz (Slot) definiert - sie kann also für verschiedene Speicherplätze unterschiedlich sein. So kann mit demselben FABI-Gerät z.B. ein Laptop über USB und ein Smartphone oder Tablet über Bluetooth angesteuert werden.
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

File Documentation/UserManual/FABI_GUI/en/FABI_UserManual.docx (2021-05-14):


# FABI - Flexible Assistive Button Interface

FABI4

# User Manual

AsTeRICS Foundation

# Table of Contents

# Welcome to FABI

FABI - the "Flexible Assistive Button Interface" - makes it possible to connect several momentary switches (buttons) to a computer or a tablet / smartphone. Pressing a button can trigger desired keys on the keyboard or carry out mouse cursor actions. A configured FABI module can be used with any computer (Windows, Linux
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

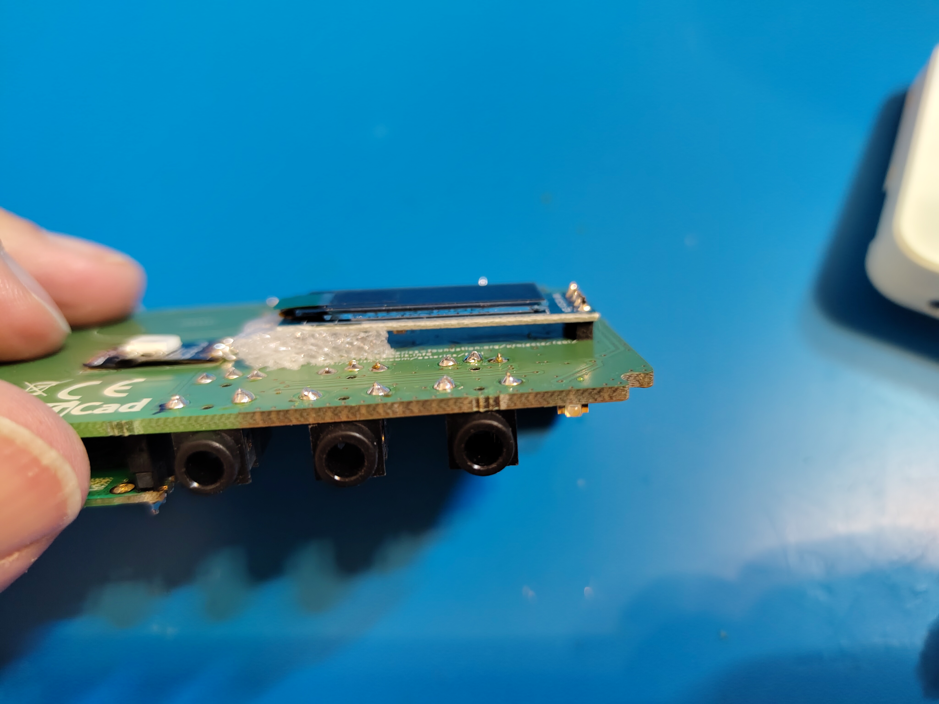
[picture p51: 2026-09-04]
Documentation/ConstructionManual/FotoBuildGuide/img/fabi3Build_16.jpg

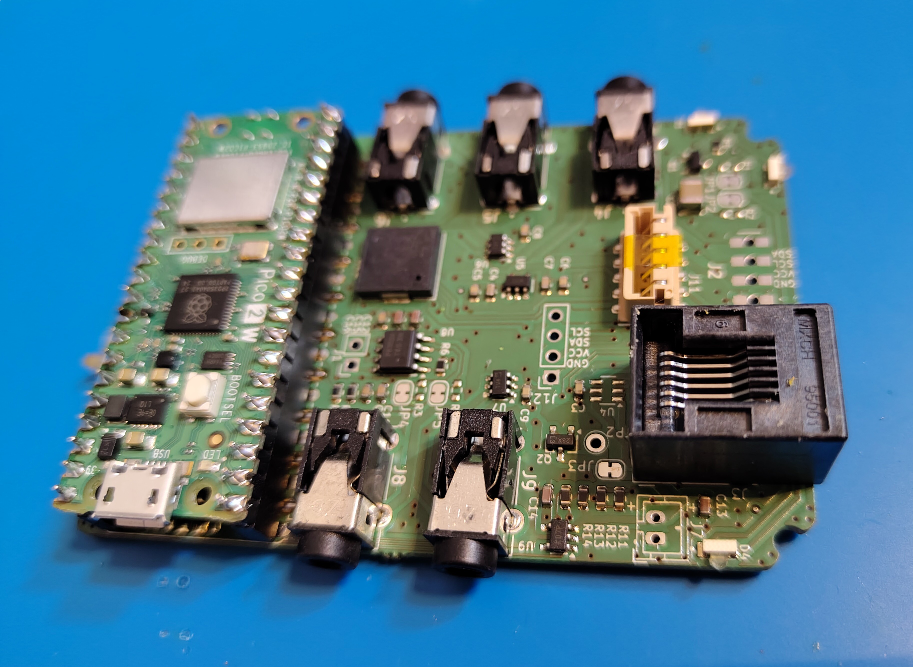
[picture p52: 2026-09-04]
Documentation/ConstructionManual/FotoBuildGuide/img/fabi3Build_08.jpg

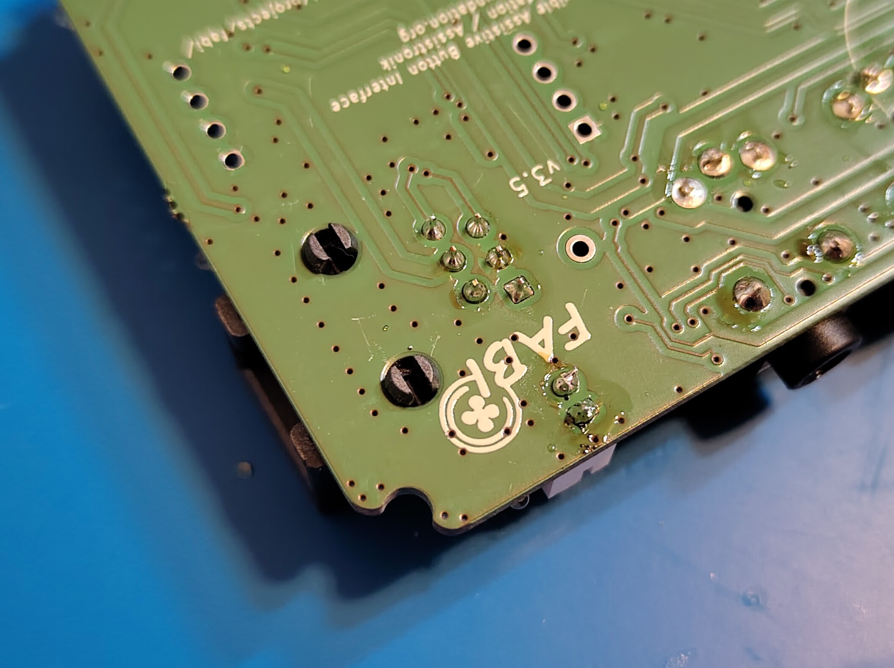
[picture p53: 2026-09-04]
Documentation/ConstructionManual/FotoBuildGuide/img/fabi3Build_13.jpg

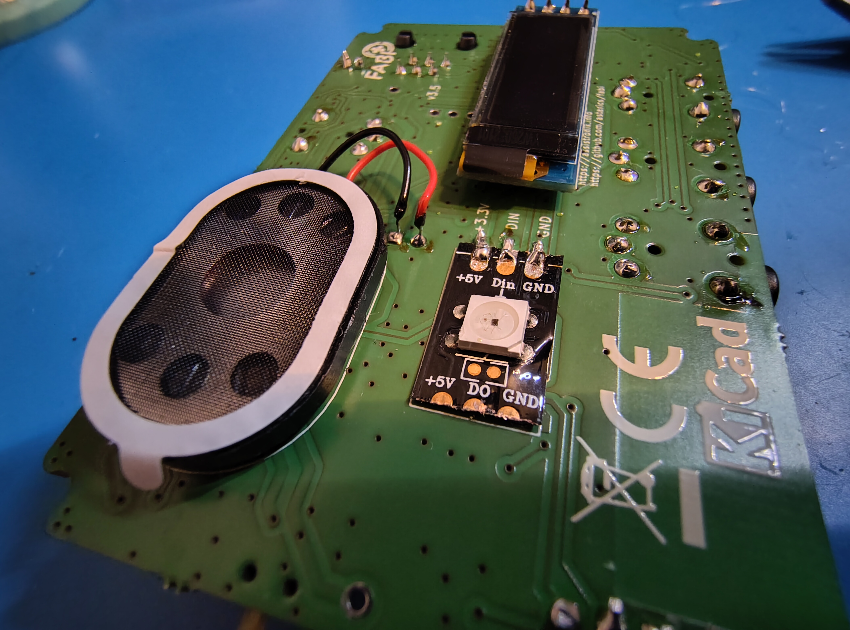
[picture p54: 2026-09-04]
Documentation/ConstructionManual/FotoBuildGuide/img/fabi3Build_21.jpg

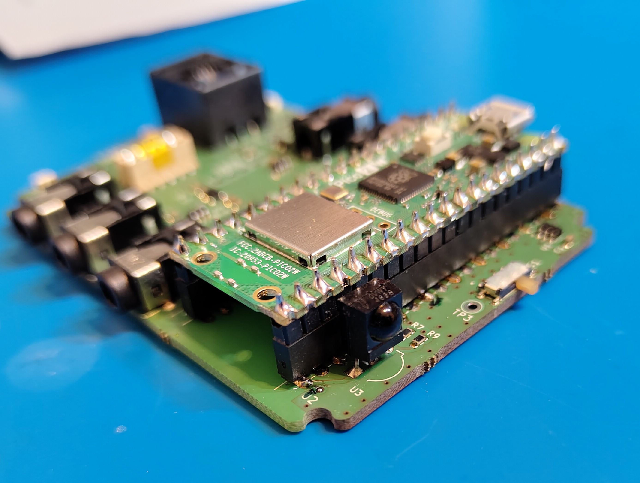
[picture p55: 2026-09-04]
Documentation/ConstructionManual/FotoBuildGuide/img/fabi3Build_10.jpg

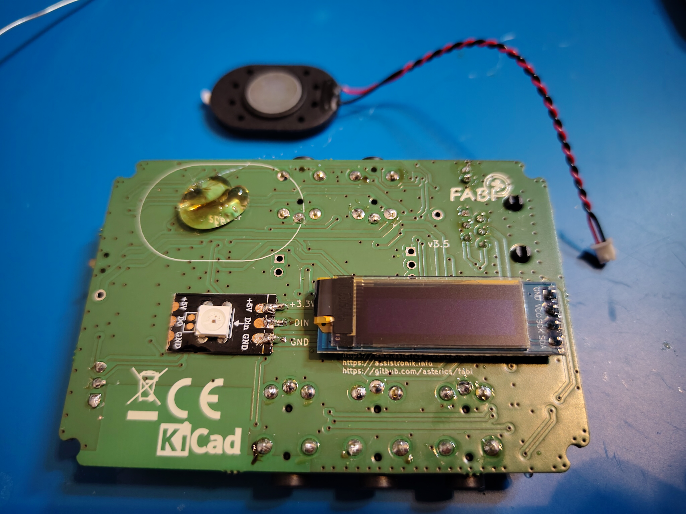
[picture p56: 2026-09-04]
Documentation/ConstructionManual/FotoBuildGuide/img/fabi3Build_19.jpg

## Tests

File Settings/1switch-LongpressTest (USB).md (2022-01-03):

## Basic information
This configuration works with 1 switch (connected to input 1).
The switch actuates the cursor-up or cursor-down key (long-press changes function).

## Function assignment

### Slot1 (name: moveUp, color: blue, mode:USB)
- Button1 = short-press: press KEY_UP (cursur up key)
- Button1 = long-press: switch to next slot 

### Slot2 (name:moveDown, color:orange, mode:USB)
- Button1 = short-press: press KEY_DOWN (cursur down key)
- Button1 = long-press: switch to next slot

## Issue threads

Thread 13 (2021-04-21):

### ISSUE TITLE
ProMicro RX/TX LEDs

### ISSUE THREAD

**Issue by benjaminaigner** [asterics/FABI#13]
When using the Bluetooth Addon, its LED is not clearly visible compared to the Arduino Pro Micro's RX/TX LEDs.

Should we switch off these LEDs?

```
pinMode(LED_BUILTIN_RX,INPUT);
pinMode(LED_BUILTIN_TX,INPUT);
```

**Comment by ChrisVeigl** [comment]
done! 
I also removed the internal LED blinking at startup ...

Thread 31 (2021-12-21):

### ISSUE TITLE
Button Action: Changing between Tabs deletes previous value

### ISSUE THREAD

**Issue by deinhofer** [asterics/FABI#31]
When opening the action of a button to (re)configure it, the currently set value is deleted as soon as you change the tab (e.g. from Mouse to Keyboard) and back again:

![grafik](https://user-images.githubusercontent.com/4621810/146185099-5e923173-0f6a-4a20-b9f4-a732d0f9c3fd.png)

This is annoying as sometimes you only want to check other options.

**Comment by ChrisVeigl** [comment]
but this only happens if do do not _save_ the changes ..
why would you switch tabs without saving and then expect the values to remain the same ?

**Comment by klues** [comment]
I agree, when switchung between the categories and nothing was changed yet, the current value should be selected, if available in the current category. I'll fix it.

**Comment by klues** [comment]
For "current value" i would understand the value currently stored in the FLipMouse, not the value I've possibly selected in the GUI before switching categories without saving.

**Comment by deinhofer** [comment]
> For "current value" i would understand the value currently stored in the FLipMouse, not the value I've possibly selected in the GUI before switching categories without saving.

Yes, I agree. It should always be in sync with the currently stored value as long as no new one was selected or saved.

**Comment by deinhofer** [comment]
> but this only happens if do do not _save_ the changes .. why would you switch tabs without saving and then expect the values to remain the same ?

because you have to open the dialog and switch the tabs to see all possible actions, when you switch back you currently saved setting is gone. This is confusing, if you don't know the old value any more and you don't know that cancelling the dialog brings back the old value.

**Comment by klues** [comment]
fixed with https://github.com/asterics/Addon-Bluetooth-WebGUI/commit/d50f7f28c21ee1daa5a362b2f63783d8b2037984
Reload `fabi.asterics.eu` twice or use `Ctrl + F5` to reload before testing in order to clear/update local offline cache.

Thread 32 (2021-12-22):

### ISSUE TITLE
Button Action: Deleting Action can't be saved

### ISSUE THREAD

**Issue by deinhofer** [asterics/FABI#32]
Deleting a keyboard action can't be saved.

![grafik](https://user-images.githubusercontent.com/4621810/146189474-ca485aba-55f8-4c39-ab27-6663f320d9ae.png)

Generally a global "Delete action" button could make sense here:

![grafik](https://user-images.githubusercontent.com/4621810/146189991-ba0efba8-813c-4c8d-b19b-4d276ed6ea6c.png)

**Comment by ChrisVeigl** [comment]
i do not understand the problem, as "Delete" shall only remove assigned keystrokes (which works IMO correctly)...

should a "Delete Action" Button assign the "no command" action  (which currently is only available in the "Device/Gerät"-Tab? - this would indeed make it easier...

**Comment by klues** [comment]
I could add a button "Delete Action", but when it's really needed?
If (a) the user can trigger this input action, then you normally would define some action for it or if (b) the user cannot trigger this input action, it's also not necessary to delete the action...

**Comment by deinhofer** [comment]
> i do not understand the problem, as "Delete" shall only remove assigned keystrokes (which works IMO correctly)...
> 
> should a "Delete Action" Button assign the "no command" action (which currently is only available in the "Device/Gerät"-Tab? - this would indeed make it easier...

But I think that's the point. First I did not realize that the "Delete" was only for deleting the keystroke field contents. I thought that I could unassign an action to this input, but this was not the case. Then I accidently recognzied that it's possible to unset an action but only in the  "Alle Kategorien" tab. I think this is not obvious.

Maybe it would even be better to directly add a delete action (waste bin icon) directly to the action list.
![grafik](https://user-images.githubusercontent.com/4621810/146827512-23baf6e8-3c21-457e-902f-b452f2324b13.png)

**Comment by ChrisVeigl** [comment]
i see!
i agree that this is a bit unintuitive!
(also that an unassigned action is called "no command" / "keine Aktion" in the All/Device tabs, but "empty"/"leer" in the action list!  - here, the same wording should be used!  

A seperate button for the "AT NC" command could indeed make sense, replacing the entries in the All/Device menus. We could call it "No Action"/"Keine Aktion" and in the list "no action"/keine Aktion" could be displayed ?

**Comment by klues** [comment]
I've now changed it to `No command (empty) // Keine Funktion (leer)` in the combobox in order to better match the wording displayed in the table. I think `empty // leer` is better in the table because it's short and therefore better visible separated from other entries.

Yes, I can add a `Clear command` button, but I'm not so sure where. I can do it like @deinhofer suggested, but to my mind this is a little bit to prominent compared to the importance (like said: how often this button really will be used?!). Additionally all the buttons at the bottom are closing the modal, while for the `Clear command` button it maybe would make more sense if it just sets the current AT-command to "No command" which then can be saved (if needed also for all slots) using the existing buttons. My suggestion would be a little wastebin icon at one of these places: https://i.imgur.com/SCuUIUd.png

**Comment by ChrisVeigl** [comment]
the wastebin icon sounds like a good idea.
i think i'd prefer the location in the combobox.

**Comment by klues** [comment]
Now implemented it like this: https://i.imgur.com/kQ3wEc3.png
It's already online, tell me, what you think.

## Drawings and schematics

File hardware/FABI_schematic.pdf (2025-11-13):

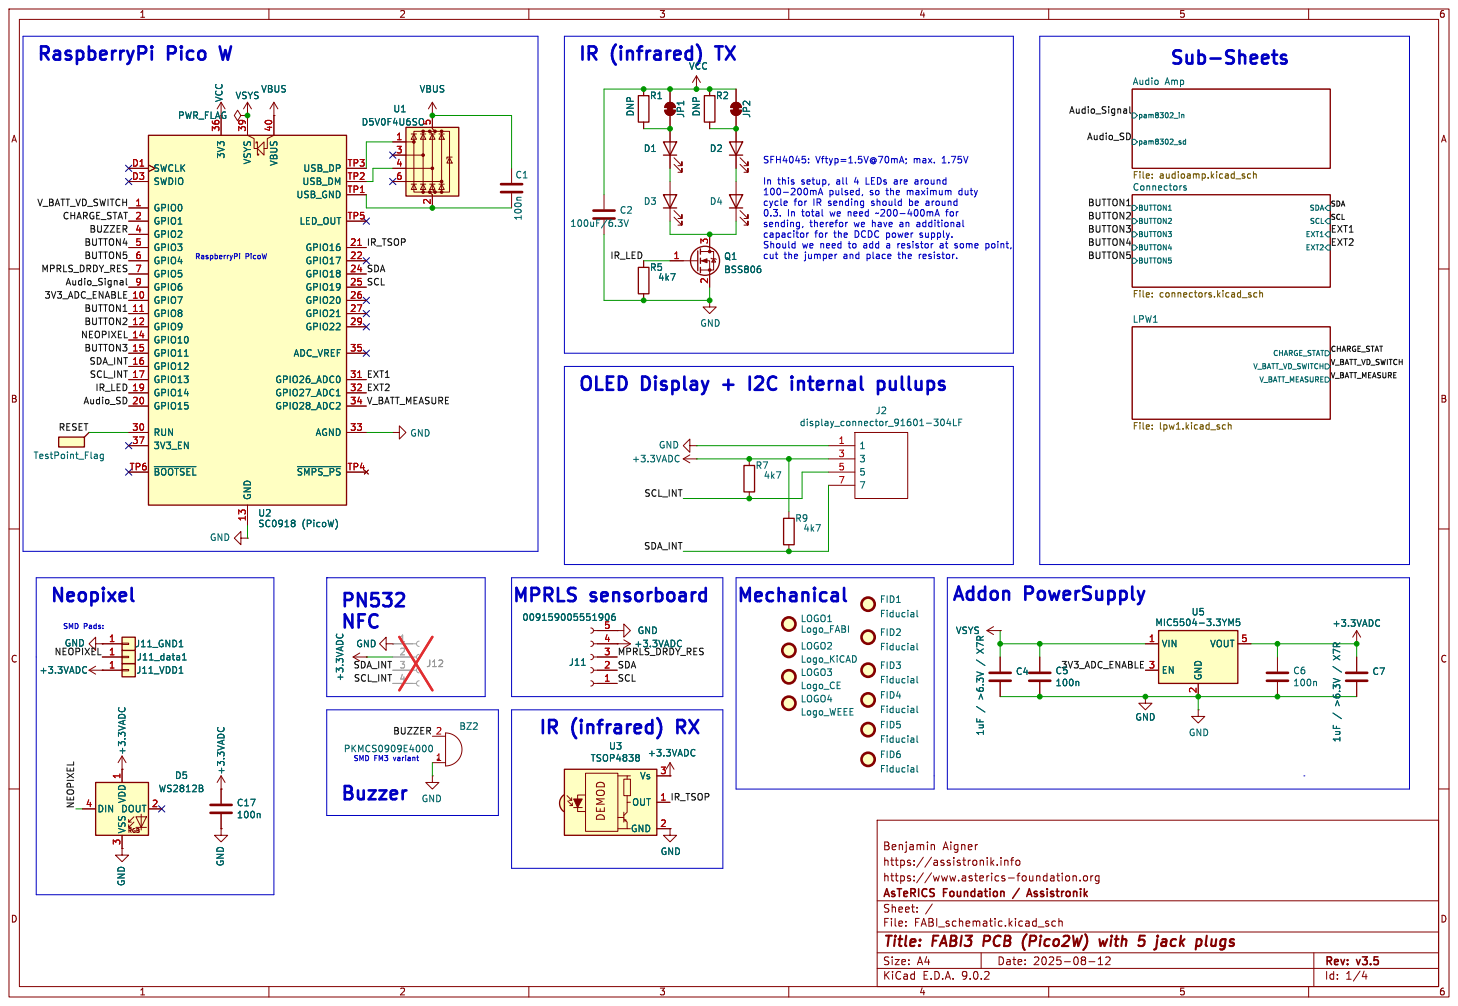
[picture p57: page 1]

pam8302_sd Audio Amp File: audioamp.kicad_sch

5 2 U2SC0918 (PicoW) SWCLK D1 SWDIO D3 GPIO0 1 GPIO1 2 GPIO2 4 GPIO3 5 GPIO4 6 GPIO5 7 GPIO6 9 GPIO7 10 GPIO8 11 GPIO9 12 GPIO10 14 GPIO11 15 GPIO12 16 GPIO13 17 GPIO14 19 GPIO15 20 RUN 30

In this setup, all 4 LEDs are around
cycle for IR sending should be around

OLED Display + I2C internal pullups

Benjamin Aigner
https://assistronik.info
https://www.asterics-foundation.org

Id: 1/4 Title: FABI3 PCB (Pico2W) with 5 jack plugs

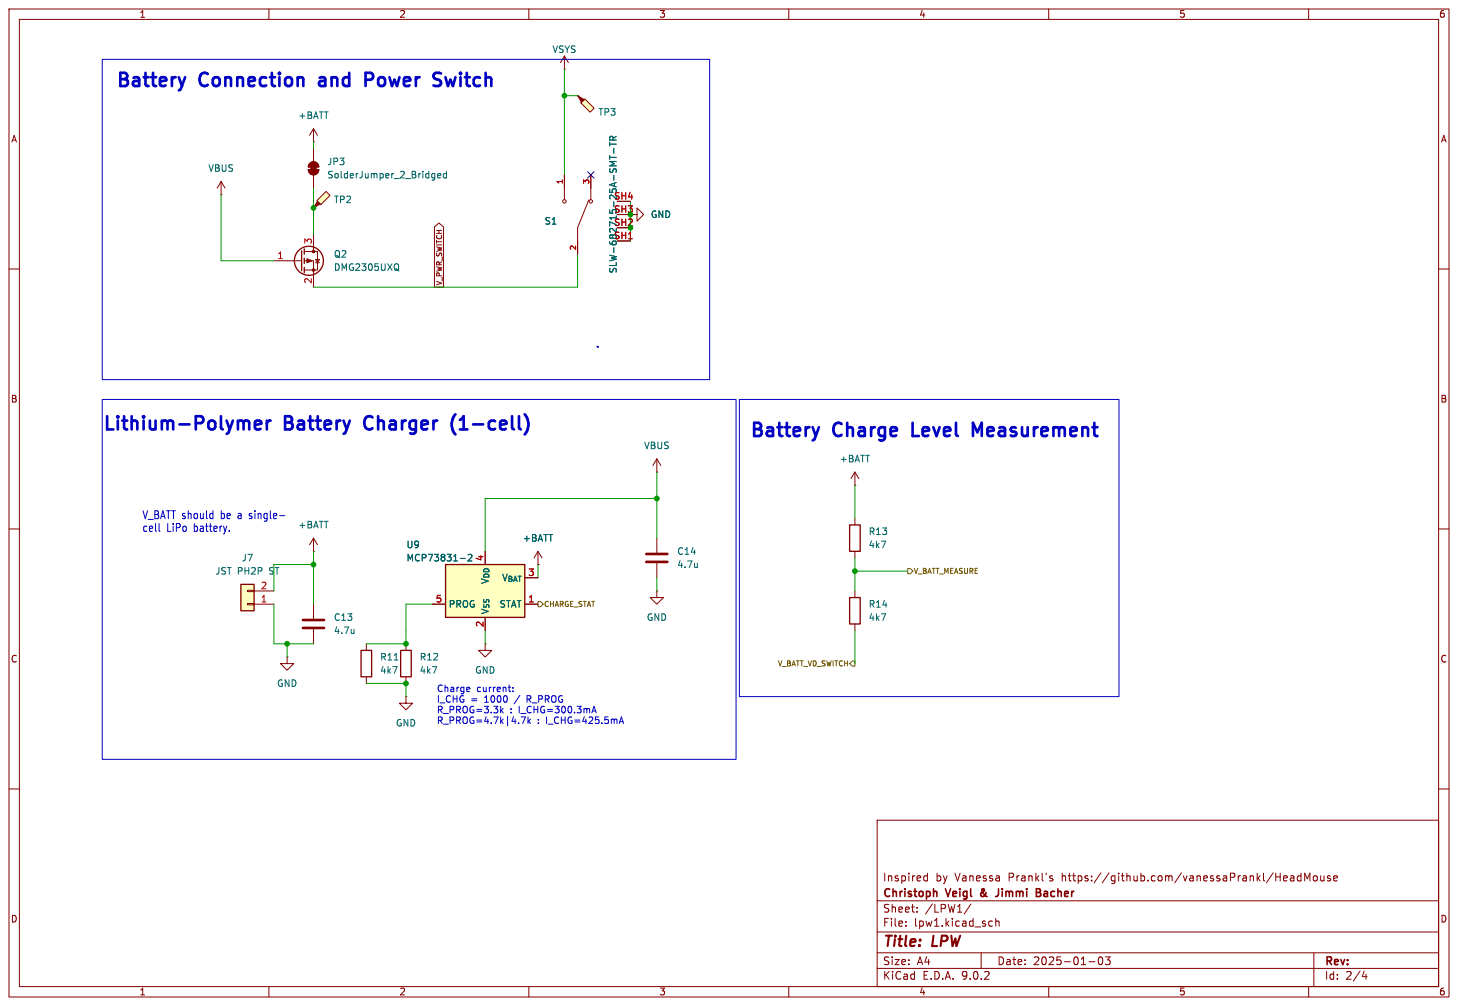
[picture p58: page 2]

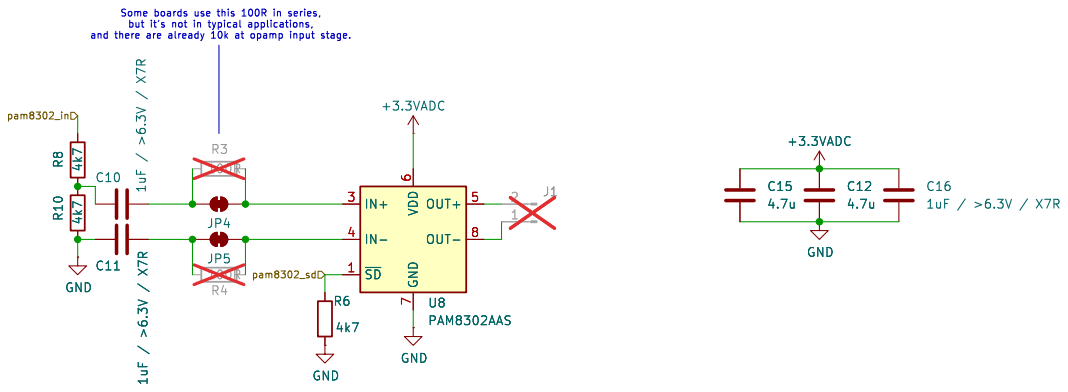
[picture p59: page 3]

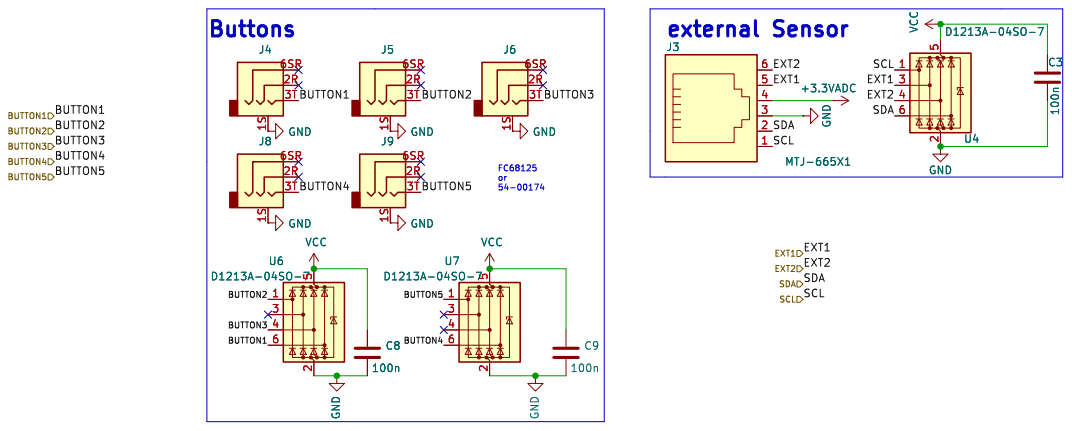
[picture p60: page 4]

Id: 4/4 Title: File: connectors.kicad_sch Sheet: /Connectors/

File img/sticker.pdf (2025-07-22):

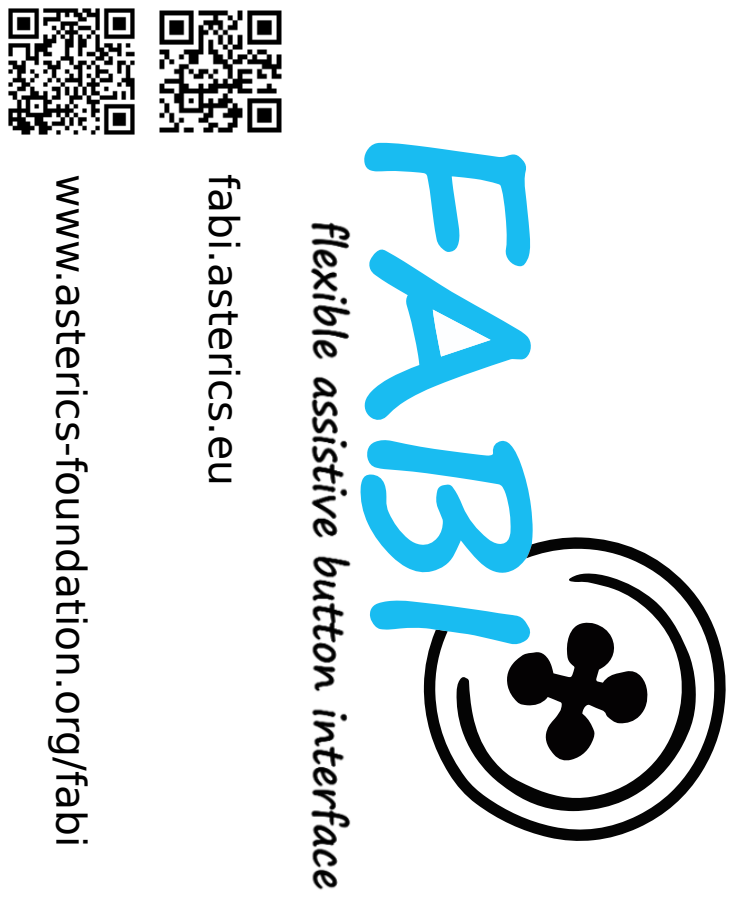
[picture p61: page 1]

www.asterics-foundation.org/fabi

fabi.asterics.eu

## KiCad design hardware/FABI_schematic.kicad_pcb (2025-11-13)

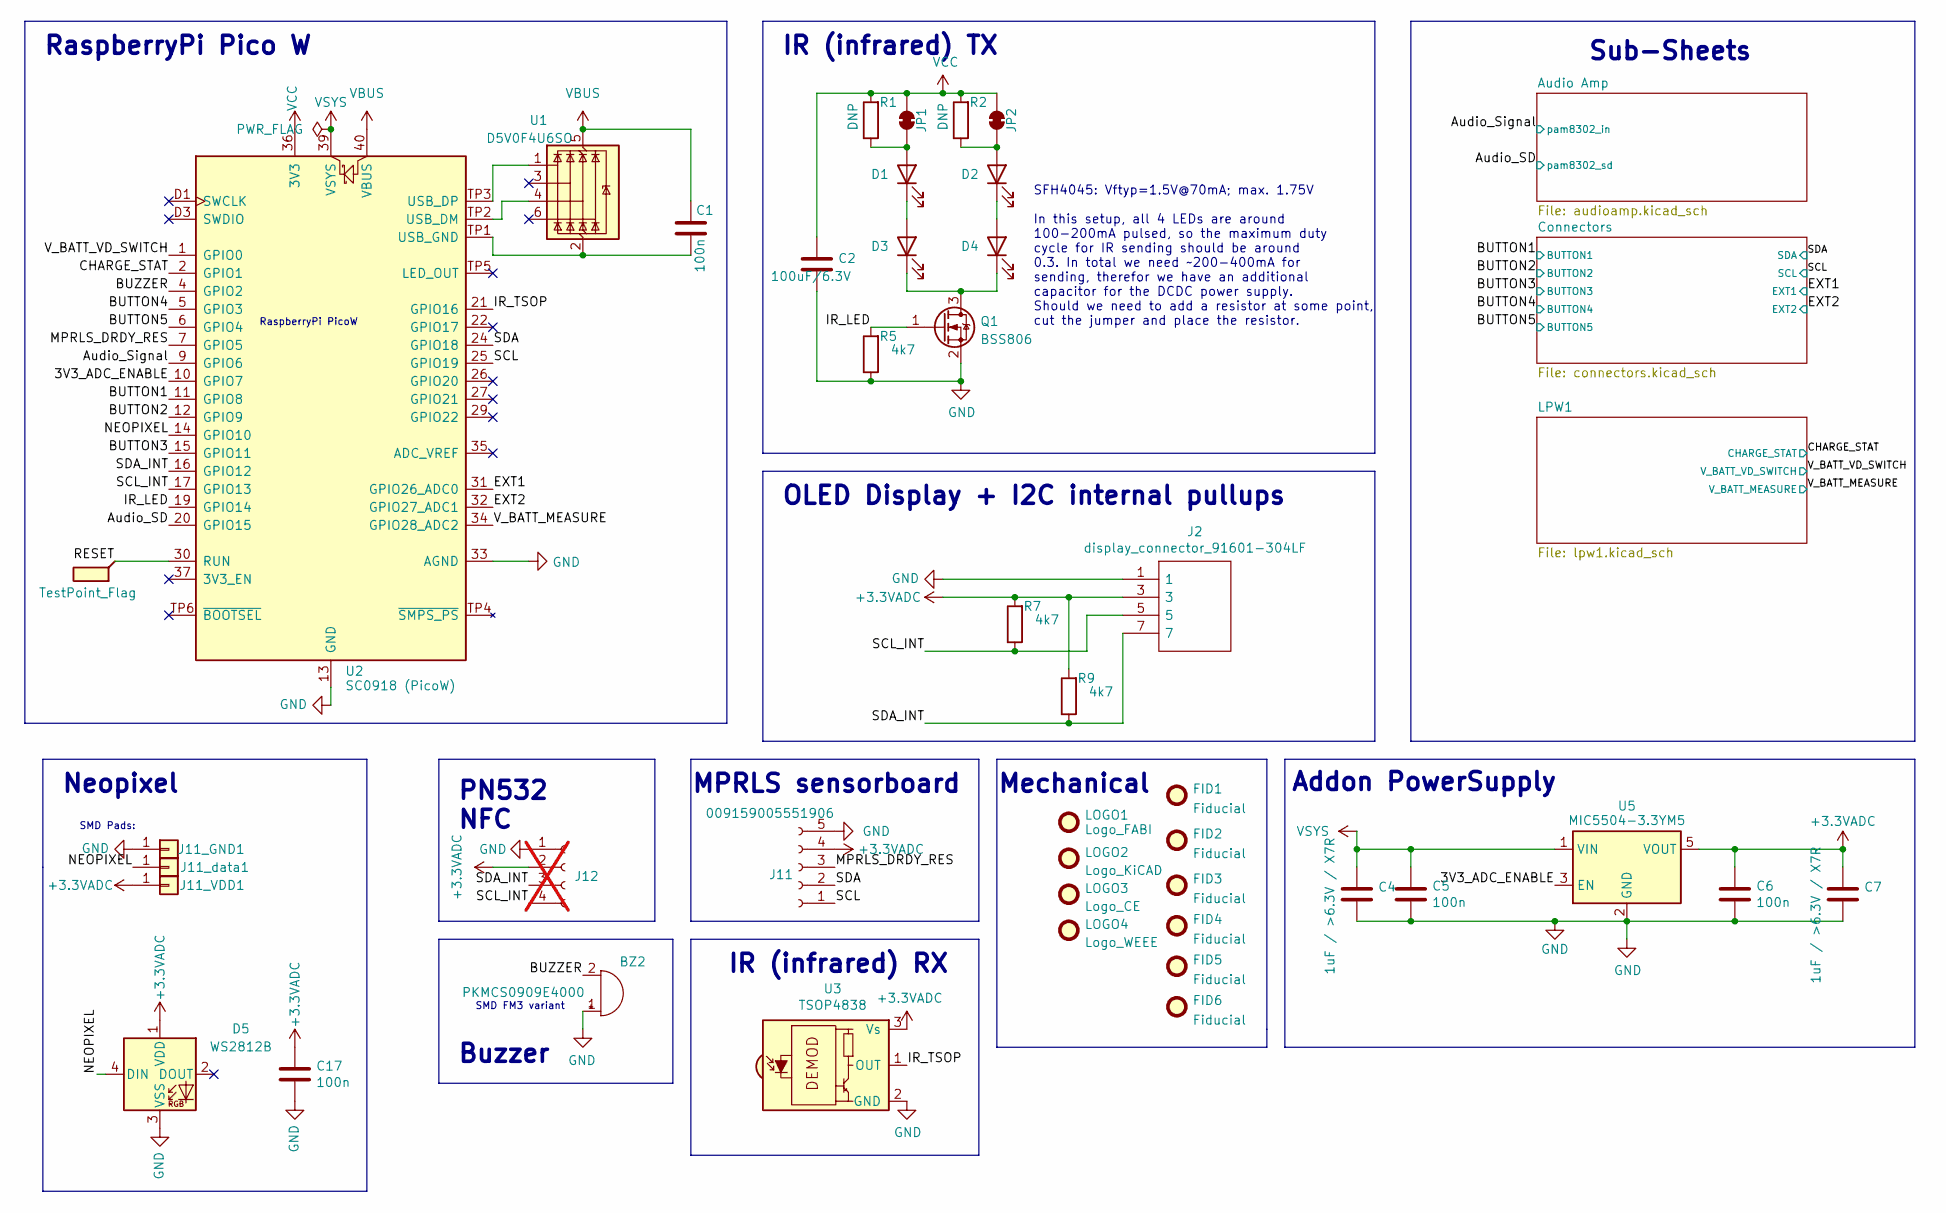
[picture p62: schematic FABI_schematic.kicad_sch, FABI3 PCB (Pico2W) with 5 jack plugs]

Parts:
BZ2: PKMCS0909E4000; Buzzer_Murata_PKMCS0909E; Digikey 490-9647-1-ND
C1, C5, C6, C17: 100n; C_0603_1608Metric; Digikey 1276-CL10B104KB8NNNLCT-ND
C2: 100uF/6.3V; C_1210_3225Metric; Digikey 1276-1092-1-ND
C4, C7: 1uF / >6.3V / X7R; C_0603_1608Metric; Digikey 1276-1019-1-ND
D1, D3: SFH4045; SFH4045N; Digikey 475-3047-1-ND
D2, D4: SFH4045; SFH4045N; Farnell 2981752
D5: WS2812B; LED_WS2812B_PLCC4_5.0x5.0mm_P3.2mm
FID1, FID2, FID3, FID4, FID5, FID6: Fiducial; Fiducial_0.5mm_Mask1mm; Digikey DNP
J2: display_connector_91601-304LF; 91601304LF; Mouser Part Number 649-91601-304LF
J11: 009159005551906; Digikey 478-8739-1-ND
J11_GND1, J11_VDD1, J11_data1: Conn_01x01_Male; SolderWirePad_1x01_SMD_1x2mm_NOPASTE
J12: Conn_01x04_Socket; PinSocket_1x04_P2.54mm_Vertical; not fitted
JP1, JP2: SolderJumper_2_Bridged; SolderJumper-2_P1.3mm_Bridged_RoundedPad1.0x1.5mm; Digikey DNP
LOGO1: Logo_FABI; FABI_Logo_s; Digikey DNP
LOGO2: Logo_KiCAD; KiCad-Logo_5mm_SilkScreen; Digikey DNP
LOGO3: Logo_CE; CE-Logo_8.5x6mm_SilkScreen; Digikey DNP
LOGO4: Logo_WEEE; WEEE-Logo_5.6x8mm_SilkScreen; Digikey DNP
Q1: BSS806; SOT-23; Digikey BSS806NH6327XTSA1CT-ND
R1, R2: DNP; R_0603_1608Metric; Farnell 3994558
R5, R7, R9: 4k7; R_0603_1608Metric; Farnell 3994558
TP1: TestPoint_Flag
U1: D5V0F4U6SO; SOT-23-6; Mouser Part Number 621-D5V0F4U6SO-7; Digikey D5V0F4U6SO-7DICT-ND
U2: SC0918 (PicoW); RaspberryPi_Pico_W_SMD_header; Digikey 2648-SC0918CT-ND
U3: TSOP4838; Vishay_MOLD-3Pin; Mouser Part Number 782-TSOP4838; Farnell 4913190
U5: MIC5504-3.3YM5; SOT-23-5; Digikey 576-4764-1-ND

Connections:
+3.3VADC: C6.1, C7.1, C17.1, D5.1 (VDD), J2.3, J11.4, J11_VDD1.1, J12.2, R7.2, R9.2, U3.3 (Vs), U5.5 (VOUT); also elsewhere on the board
/3V3_ADC_ENABLE: U2.10 (GPIO7), U5.3 (EN)
/Audio_SD: U2.20 (GPIO15); also elsewhere on the board
/Audio_Signal: U2.9 (GPIO6); also elsewhere on the board
/BUTTON1: U2.11 (GPIO8); also elsewhere on the board
/BUTTON2: U2.12 (GPIO9); also elsewhere on the board
/BUTTON3: U2.15 (GPIO11); also elsewhere on the board
/BUTTON4: U2.5 (GPIO3); also elsewhere on the board
/BUTTON5: U2.6 (GPIO4); also elsewhere on the board
/BUZZER: BZ2.2 (-), U2.4 (GPIO2)
/CHARGE_STAT: U2.2 (GPIO1); also elsewhere on the board
/EXT1: U2.31 (GPIO26_ADC0); also elsewhere on the board
/EXT2: U2.32 (GPIO27_ADC1); also elsewhere on the board
/IR_LED: Q1.1 (G), R5.2, U2.19 (GPIO14)
/IR_TSOP: U2.21 (GPIO16), U3.1 (OUT)
/MPRLS_DRDY_RES: J11.3, U2.7 (GPIO5)
/NEOPIXEL: D5.4 (DIN), J11_data1.1, U2.14 (GPIO10)
/RESET: TP1.1, U2.30 (RUN)
/SCL: J11.1, U2.25 (GPIO19); also elsewhere on the board
/SCL_INT: J2.5, J12.4, R7.1, U2.17 (GPIO13)
/SDA: J11.2, U2.24 (GPIO18); also elsewhere on the board
/SDA_INT: J2.7, J12.3, R9.1, U2.16 (GPIO12)
/V_BATT_MEASURE: U2.34 (GPIO28_ADC2); also elsewhere on the board
/V_BATT_VD_SWITCH: U2.1 (GPIO0); also elsewhere on the board
GND: BZ2.1 (+), C2.2, C4.2, C5.2, C6.2, C7.2, C17.2, D5.3 (VSS), J2.1, J11.5, J11_GND1.1, J12.1, Q1.2 (S), R5.1, U2.3 (GND), U2.8 (GND), U2.13 (GND), U2.18 (GND), U2.23 (GND), U2.28 (GND), U2.33 (AGND), U2.38 (GND), U2.D2 (GND), U3.2 (GND), U5.2 (GND); also elsewhere on the board
unnamed: D1.2 (A), JP1.2 (B), R1.1
unnamed: D1.1 (K), D3.2 (A)
unnamed: D2.2 (A), JP2.2 (B), R2.1
unnamed: D2.1 (K), D4.2 (A)
unnamed: D3.1 (K), D4.1 (K), Q1.3 (D)
unnamed: C1.2, U1.2 (GND), U2.TP1 (USB_GND)
unnamed: U1.1 (I/O1), U2.TP3 (USB_DP)
unnamed: U1.4 (I/O3), U2.TP2 (USB_DM)
VBUS: C1.1, U1.5 (VBUS), U2.40 (VBUS); also elsewhere on the board
VCC: C2.1, JP1.1 (A), JP2.1 (A), R1.2, R2.2, U2.36 (3V3); also elsewhere on the board
VSYS: C4.1, C5.1, U2.39 (VSYS), U5.1 (VIN); also elsewhere on the board

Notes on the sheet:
PN532 NFC
IR (infrared) RX
Mechanical
Addon PowerSupply
RaspberryPi PicoW
RaspberryPi Pico W
Neopixel
SFH4045: Vftyp=1.5V@70mA; max. 1.75V In this setup, all 4 LEDs are around 100-200mA pulsed, so the maximum duty cycle for IR sending should be around 0.3. In total we need ~200-400mA for sending, therefor we have an additional capacitor for the DCDC power supply. Should we need to add a resistor at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
MPRLS sensorboard
SMD Pads:
Buzzer
SMD FM3 variant
IR (infrared) TX
Sub-Sheets
OLED Display + I2C internal pullups

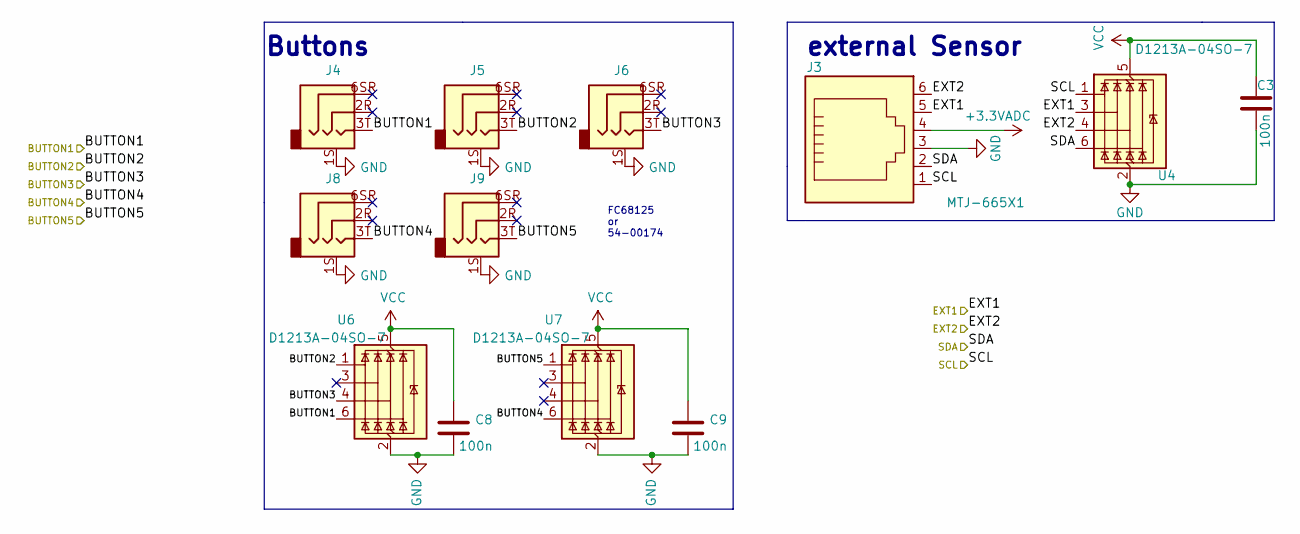
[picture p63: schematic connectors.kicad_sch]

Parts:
C3, C8, C9: 100n; C_0603_1608Metric; Digikey 1276-CL10B104KB8NNNLCT-ND
J3: MTJ-665X1; RJ12_Amphenol_54601-x06_Horizontal; Digikey 2057-MTJ-665X1-ND
J4, J5, J6, J8, J9: 54-00174 / FC68125; FC68125; Digikey 839-54-00174CT-ND
U4, U6, U7: D1213A-04SO-7; SOT-23-6; Digikey D1213A-04SO-7DICT-ND

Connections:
+3.3VADC: J3.4; also elsewhere on the board
/BUTTON1: J4.3T, U6.6 (I/O4); also elsewhere on the board
/BUTTON2: J5.3T, U6.1 (I/O1); also elsewhere on the board
/BUTTON3: J6.3T, U6.4 (I/O3); also elsewhere on the board
/BUTTON4: J8.3T, U7.6 (I/O4); also elsewhere on the board
/BUTTON5: J9.3T, U7.1 (I/O1); also elsewhere on the board
/EXT1: J3.5, U4.3 (I/O2); also elsewhere on the board
/EXT2: J3.6, U4.4 (I/O3); also elsewhere on the board
/SCL: J3.1, U4.1 (I/O1); also elsewhere on the board
/SDA: J3.2, U4.6 (I/O4); also elsewhere on the board
GND: C3.2, C8.2, C9.2, J3.3, J4.1S, J5.1S, J6.1S, J8.1S, J9.1S, U4.2 (GND), U6.2 (GND), U7.2 (GND); also elsewhere on the board
VCC: C3.1, C8.1, C9.1, U4.5 (VBUS), U6.5 (VBUS), U7.5 (VBUS); also elsewhere on the board

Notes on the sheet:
Buttons
FC68125 or 54-00174
external Sensor

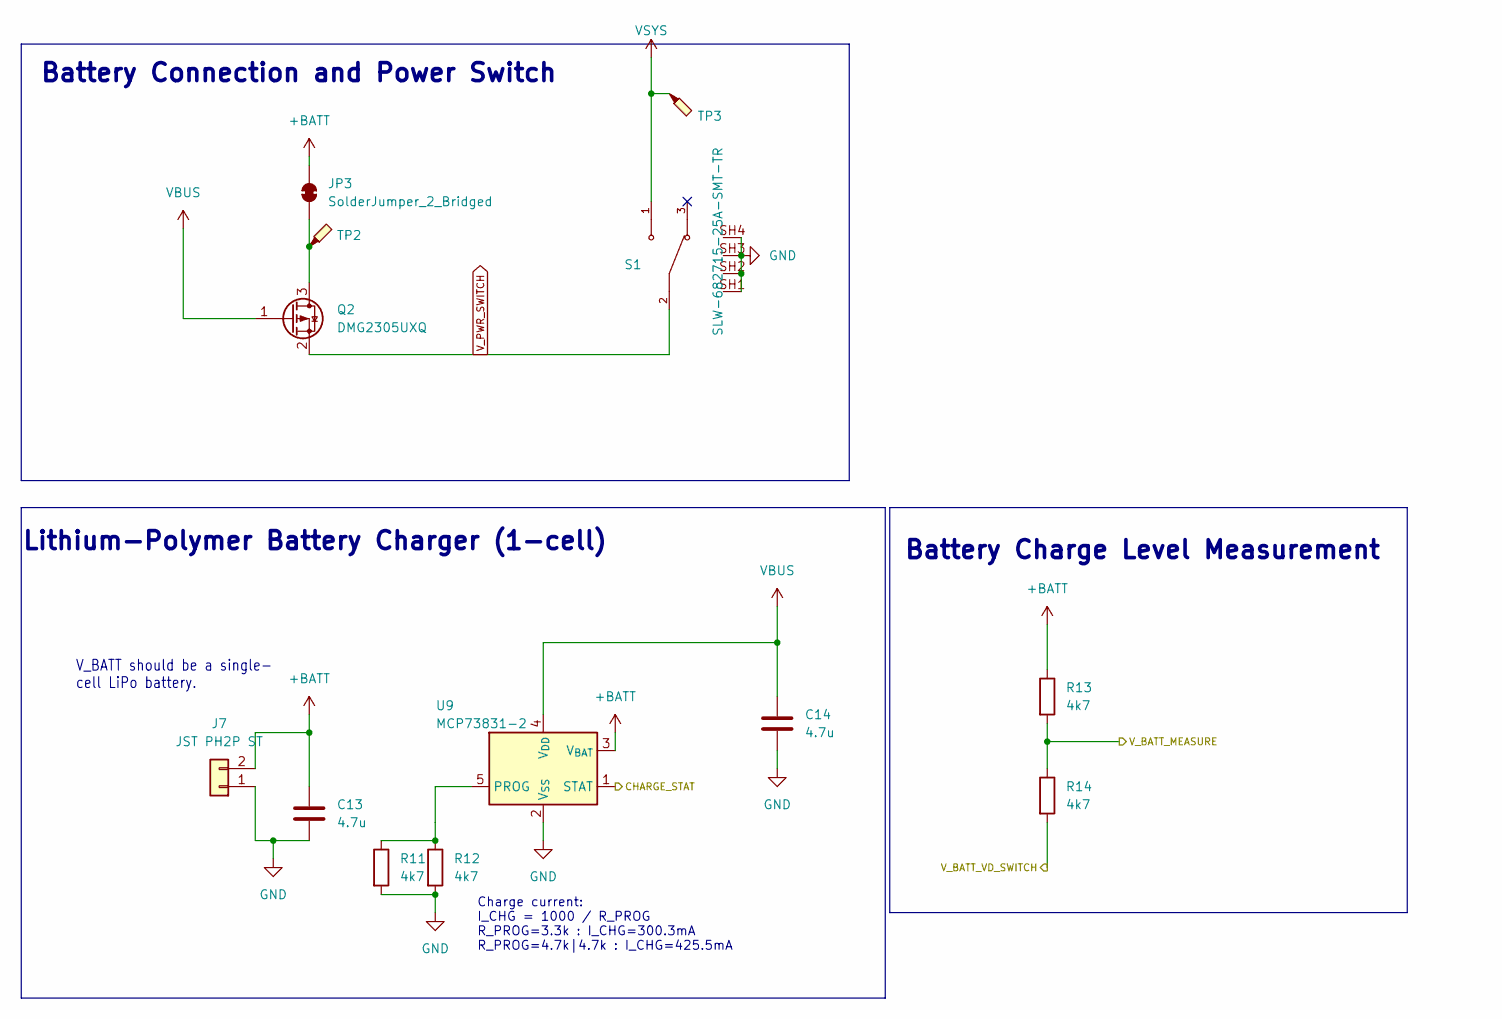
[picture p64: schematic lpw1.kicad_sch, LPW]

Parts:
C13, C14: 4.7u; C_0603_1608Metric; Mouser 81-GRM188Z71A475KE5J
J7: JST PH2P ST; JST_PH_B2B-PH-K_1x02_P2.00mm_Vertical
JP3: SolderJumper_2_Bridged; SolderJumper-2_P1.3mm_Bridged_RoundedPad1.0x1.5mm
Q2: DMG2305UXQ; TSOT-23
R11, R12: 4k7; R_0603_1608Metric; Mouser Part Number 708-RMCF0603FT3K30; Digikey RMCF0603FT3K30TR-ND
R13, R14: 4k7; R_0603_1608Metric; Mouser Part Number ERJ-PA3J121V; Digikey P120BZTR-ND
S1: SLW-682715-25A-SMT-TR; SW_SLW-682715-25A-SMT-TR; PARTREV 1.01
TP2, TP3: TestPoint_THTPad_D2.0mm_Drill1.0mm
U9: MCP73831-2; SOT-23-5; Mouser Part Number 579-MCP73831T-2ACIOT; Mouser MCP73831T-2ACI/OT

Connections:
+BATT: C13.1, J7.2, JP3.2 (B), R13.1, U9.3 (V_{BAT})
/CHARGE_STAT: U9.1 (STAT); also elsewhere on the board
/V_BATT_MEASURE: R13.2, R14.1; also elsewhere on the board
/V_BATT_VD_SWITCH: R14.2; also elsewhere on the board
GND: C13.2, C14.2, J7.1, R11.2, R12.2, S1.SH1, S1.SH2, S1.SH3, S1.SH4, U9.2 (V_{SS}); also elsewhere on the board
unnamed: JP3.1 (A), Q2.3 (D), TP2.1
unnamed: R11.1, R12.1, U9.5 (PROG)
VBUS: C14.1, Q2.1 (G), U9.4 (V_{DD}); also elsewhere on the board
VSYS: S1.1, TP3.1; also elsewhere on the board
V_PWR_SWITCH: Q2.2 (S), S1.2

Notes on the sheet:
Battery Charge Level Measurement
Battery Connection and Power Switch
Lithium-Polymer Battery Charger (1-cell)
Charge current: I_CHG = 1000 / R_PROG R_PROG=3.3k : I_CHG=300.3mA R_PROG=4.7k|4.7k : I_CHG=425.5mA
V_BATT should be a single- cell LiPo battery.

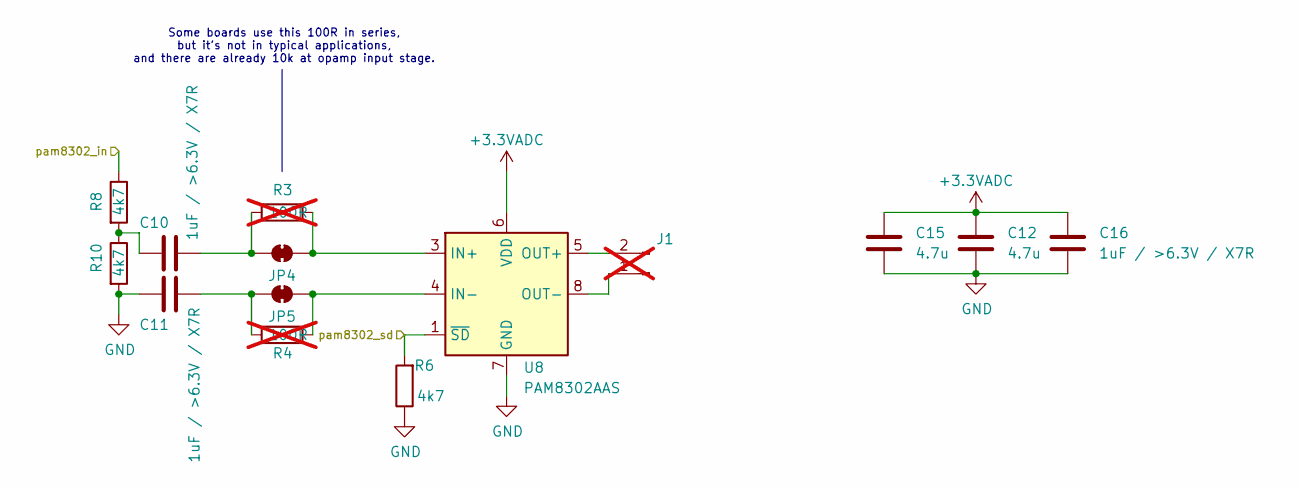
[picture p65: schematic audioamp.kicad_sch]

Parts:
C10, C11: 1uF / >6.3V / X7R; C_0603_1608Metric; Digikey 1276-1019-1-ND
C12, C15: 4.7u; C_0603_1608Metric; Mouser 81-GRM188Z71A475KE5J
C16: 1uF / >6.3V / X7R; C_0603_1608Metric; Mouser 81-GRM188Z71A475KE5J
J1: PinSocket_1x02_P2.54mm_Vertical; not fitted
JP4, JP5: SolderJumper_2_Bridged; SolderJumper-2_P1.3mm_Bridged_RoundedPad1.0x1.5mm; Digikey DNP
R3, R4: 100R; R_0603_1608Metric; Farnell 3994558; not fitted
R6: 4k7; R_0603_1608Metric; Farnell 3994558
R8, R10: 4k7; R_0603_1608Metric; Mouser Part Number 71-RCA060310K0FKEA; Farnell 2616584
U8: PAM8302AAS; SOIC-8_3.9x4.9mm_P1.27mm; Mouser Part Number 621-PAM8302AASCR; Farnell 3373819

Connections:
+3.3VADC: C12.1, C15.1, C16.1, U8.6 (VDD); also elsewhere on the board
/Audio_SD: R6.2, U8.1 (~SD); also elsewhere on the board
/Audio_Signal: R8.1; also elsewhere on the board
GND: C11.1, C12.2, C15.2, C16.2, R6.1, R10.2, U8.7 (GND); also elsewhere on the board
unnamed: C10.1, R8.2, R10.1
unnamed: J1.1, U8.8 (OUT-)
unnamed: J1.2, U8.5 (OUT+)
unnamed: JP4.1 (A), R3.1, U8.3 (IN+)
unnamed: C10.2, JP4.2 (B), R3.2
unnamed: JP5.1 (A), R4.1, U8.4 (IN-)
unnamed: C11.2, JP5.2 (B), R4.2

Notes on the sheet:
Some boards use this 100R in series, but it's not in typical applications, and there are already 10k at opamp input stage.

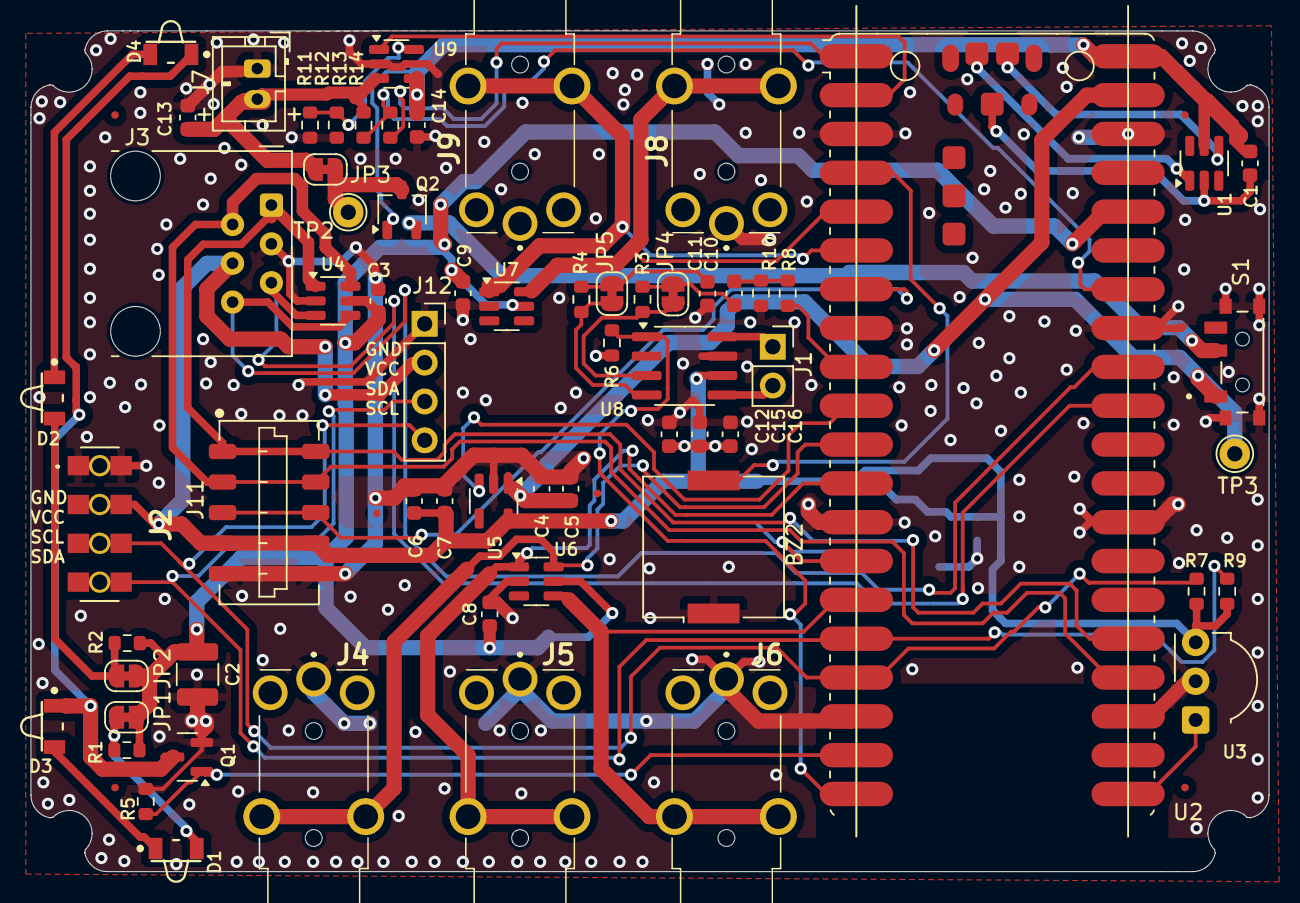
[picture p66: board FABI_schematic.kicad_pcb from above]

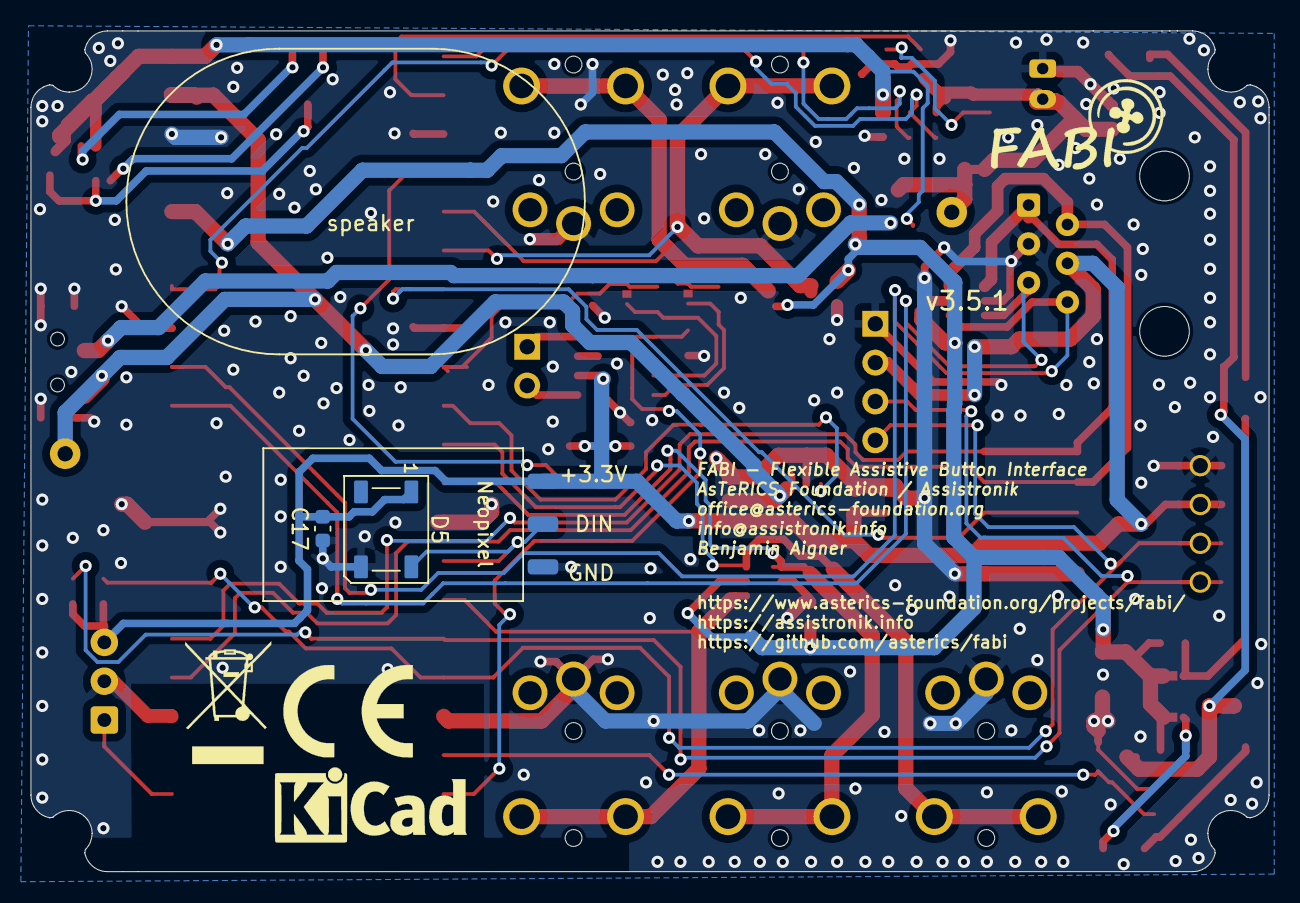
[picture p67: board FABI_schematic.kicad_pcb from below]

Board: 2 copper layers, 81.0 x 55.0 mm, 80 parts (9 on the bottom side), 46 nets.

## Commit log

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2019-09-25 Added FABI boxes & button designs (FreeCAD) with exported STL files
    [FABI.fcstd, button_24mm.stl, button_30mm.stl, fabi_base.stl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]
2019-09-27 Added a FABI schematic
    [FABI_schematic.kicad_pcb, FABI_schematic.sch]
2019-10-17 Added microswitch, moved button designs into different folders
    [ALPS_button.fcstd, button_24mm.stl, button_30mm.stl]
2019-10-17 Added STL file for microswitch
    [ALPS_button.stl]
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2020-08-15 Moved schematic into new folder, added README
    [FABI_schematic.kicad_pcb, FABI_schematic.sch]
2020-08-20 Added first PCB draft
    [FABI_schematic.kicad_pcb, FABI_schematic.sch]
2020-08-24 Added logos
    [FABI_schematic.kicad_pcb]
2020-08-27 Removed ESP32 from FABI PCB, we will use the FM BT Addon. Added QR codes to UserManual & Releases
    [FABI_schematic.kicad_pcb, FABI_schematic.sch]
2020-08-31 Added Neopixel & MPX pressure sensor to PCB.
    [FABI_schematic.kicad_pcb, FABI_schematic.sch]
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2021-02-01 redesign of PCB, Jackplugs updatet, Buzzer added, TVS repositioned
    [CUI_DEVICES_CMI-9605IC-0380T.step, FABI_schematic.kicad_pcb, FABI_schematic.sch]
2021-02-01 new schematics PDF
    [FABI_schematic.sch]
2021-02-01 +Display header & 3D design of display to find position Signed-off-by: fussthalerandreas <fussthaler.andreas1997@gmail.com>
    [FABI_schematic.kicad_pcb, FABI_schematic.sch]
2021-02-02 v2 of the PCB: added: Diplay connector, buzzer replaced: JackPlugs repositioned: JackPlugs, TVS, NeoPixel connector, pressure sensor
    [FABI_schematic.kicad_pcb, FABI_schematic.sch, OLED092_display.step, ProMicro.step]
2021-02-04 SMD types of components added, TVS diode orientation, PullUps I2C Signed-off-by: fussthalerandreas <fussthaler.andreas1997@gmail.com>
    [FABI_schematic.kicad_pcb, FABI_schematic.sch]
2021-02-04 JackPlug Footprint changed
    [FABI_schematic.kicad_pcb, FABI_schematic.sch, JackPlug_FC68125.step]
2021-02-04 Pins changed and connected to AddOn
    [FABI_schematic.kicad_pcb, FABI_schematic.sch]
2021-02-08 Display positioning: adding adapted PinSocket to enable soldering and pluggin in of the display, 3D Models adapted
    [FABI_schematic.kicad_pcb, FABI_schematic.sch]
2021-02-11 routed the PCB, adapted all components, ready for review
    [FABI_schematic.kicad_pcb, FABI_schematic.sch]
2021-02-12 PCB v2, after Feedback (according to Meeting 2)
    [FABI.fcstd, FABI_schematic.kicad_pcb, FABI_schematic.sch]
2021-02-15 adapted PCB according to Feedback (mounting holes, ProMicro pins enlarged, TVS-diods and arrays repositioned and routes enlarged to 0.5mm, NeoPixel SMD Pads, +element labels)
    [FABI_schematic.kicad_pcb, FABI_schematic.sch]
2021-02-17 updated PCB edges, to mount PCB with M3 screws, minor changes to size and some element positions, SMD NeoPixel pads updated
    [FABI.fcstd, FABI_schematic.sch]
2021-02-17 JackPlugs in Schematic changed
    [FABI_schematic.kicad_pcb, FABI_schematic.sch]
2021-02-18 ProMicro and most inner components of the PCB shifted to the right by 1.5mm new Buzzer (12mm diameter) Schematics: order infos added & JackPlugs changed
    [FABI_PCB_BOM.csv, FABI_schematic.kicad_pcb, FABI_schematic.sch]
2021-02-19 PCB enlargede up by 1 mm per (long) side & JackPlugs distance reduced (0.5mm) --> getting space for mounting in 3D case Logos and Texts added on Silkscreen
    [FABI_schematic.kicad_pcb]
2021-02-21 small final adjustment (Silk placements) before production of first prototype
    [FABI_schematic.kicad_pcb, FABI_schematic.sch]
2021-02-22 BOM-Export and elemnt property adjustments
    [FABI_schematic.sch]
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2021-03-17 PCB: JackPlug footprint adapted: adjuste plastic konb
    [FABI_logo.step, FABI_schematic.kicad_pcb, FABI_schematic.sch]
2021-03-19 PCB update: Footprints and Buzzer Resistior
    [FABI_schematic.kicad_pcb, FABI_schematic.sch]
2021-03-19 +) FABI PCB 3D Printing Case
    [FABI_top_1.stl, FABI_top_stronger.stl, FABIv2.FCStd]
2021-03-24 3D casing for PCB version: bottom part created and min changes in top part, PCB and BOM updated (4,7k -> 10k)
    [FABI_bottom_3.stl, FABI_schematic.kicad_pcb, FABI_schematic.sch, FABI_top_3.stl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]
2021-03-25 3D case: +) hole for pressureLine
    [FABIv2.FCStd]
2021-04-02 major changes in case design: tolernace for mounting, new mounting line and thinner wall (change in top and bottom part), logo orientation, height of bottom,
    [FABI_buttom_5.stl, FABI_top_5.stl, FABIv2.FCStd]
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2021-04-08 Silkscreen updates
    [FABI_schematic.kicad_pcb]
2021-04-12 PCB: buzzer Resistor & silkscreen updates
    [FABI_schematic.sch]
2021-04-12 changed pinheader for Addon to 5x2
    [FABI_schematic.sch]
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2021-04-20 removed obsolete stl and BackUp files exported 4 files (with and without Display and PressureLineHole)
    [FABI_PCB_Bottom_withPressureHole.stl, FABI_bottom_3.stl, FABI_buttom_5.stl, FABI_top_1.stl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]
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2021-04-29 Case Changes: *) Bottom: repositioned USB light cut *) Top: adjusted Display cut for AZ-Delivery and bigger displays
    [FABI_PCB_Bottom_withPressureHole.stl]
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2021-05-05 minor change in display cut: reduced height of cableCut
    [FABI_PCB_Top.stl]
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2021-06-26 Changed power for MPX,Neopixel and Addon from RAW pin to VCC pin, RAW pin is connected via a diode, so ~VUSB-0.6V; VCC is directly connected to VUSB (for 5V version)
    [FABI_schematic.kicad_pcb, FABI_schematic.sch]
2021-11-18 Changed buzzer footprint to cheaper, smaller and tone-capable buzzer
    [FABI_schematic.kicad_pcb, FABI_schematic.sch]
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2022-09-20 Added GND/VCC planes to PCB & updated to KiCAD 6
    [FABI_schematic.kicad_pcb]
2022-11-30 Moved FreeCAD Design for buttons to a dedicated file; removed mounting holes on buttons (not very 3D printer-friendly)
    [FABI.fcstd, arcade_buttons.FCStd, button_24mm.stl, button_30mm.stl]
2023-07-12 Moved button designs to: https://github.com/asterics/buttondesigns
    [ALPS_button.fcstd, ALPS_button.stl, arcade_buttons.FCStd, button_24mm.stl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]
2023-07-12 First PCB draft of FABI3
    [FABI_schematic.kicad_pcb, FABI_schematic.kicad_sch]
2023-07-13 silkscreen changes
    [FABI_schematic.kicad_pcb]
2023-07-14 Updated PCB to move MPRLS connector away from PicoW; rerouted and exported STEP
    [FABI_schematic.kicad_pcb]
2023-07-17 Changed TVS array to a bigger one, cleaned up libraries
    [FABI_schematic.kicad_pcb, FABI_schematic.kicad_sch]
2023-07-17 Updated case for FABI3 PCB
    [FABI_PCB_Bottom.stl, FABI_PCB_Top.stl]
2023-07-18 Fixed stencil & some DRC errors
    [FABI_schematic.kicad_pcb]
2023-07-18 Changed footprint in SCH as well
    [FABI_schematic.kicad_sch]
2023-07-18 More engraving of logo & text; added chamfer on screw holes (better printing; no overhang)
    [FABI_PCB_Bottom.stl, FABI_PCB_Top.stl, FABIv3.FCStd]
2023-07-18 Added note on replacement jack plugs & added iBOM
    [FABI_schematic.kicad_sch]
2023-07-19 Adapted BOM in SCH; added new ConstructionManual PDF
    [FABI_schematic.kicad_sch]
2023-07-24 Major cleanup of unused v1 & v2 stuff; directory cleanup
    [CUI_DEVICES_CMI-9605IC-0380T.step, FABI.fcstd, FABI_PCB_BOM.csv, FABI_PCB_Bottom.stl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]
2023-08-08 Added a small cutout for PicoW
    [FABI_PCB_Bottom.stl, FABIv3.FCStd]
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2023-08-23 Changed extension plug from 3.5mm to RJ25. Updated iBOM (excluding some stuff)
    [FABI_schematic.kicad_pcb, FABI_schematic.kicad_sch]
2023-08-25 Updated SCH pdf, changed copper polygon
    [FABI_schematic.kicad_pcb]
2023-08-25 Minor PCB fix
    [FABI_schematic.kicad_pcb]
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2023-09-13 Added 3d model & order numbers for RJ25
    [FABI_schematic.kicad_pcb, FABI_schematic.kicad_sch]
2023-09-13 Changed case for RJ25 cutout
    [FABI_PCB_Bottom.stl, FABI_PCB_Top.stl]
2023-09-13 Changed TSOP cutout for better printability (smaller)
    [FABI_PCB_Bottom.stl]
2024-02-28 Added CSV BOM; added 3D model of RJ25
    [FABI_schematic.csv]
2024-03-18 added sanitized BOM file with annotations regarding supplier
    [FABI_PCB_BOM.ods]
2024-03-18 added link to DIY tutorial
    [FABI_PCB_BOM.ods]
2024-03-19 removed 3pin header for Neopixel from BOM, not placed
    [FABI_PCB_BOM.ods]
2024-05-29 Added NFC pin header & silkscreen markings for I2C
    [FABI_schematic.kicad_pcb, FABI_schematic.kicad_sch]
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2025-06-30 Fixed some messed up labels (imports from EAGLE); cleaned up unused libs
    [CUI_DEVICES_CMI-9605IC-0380T.step, FABI_schematic.kicad_pcb, FABI_schematic.kicad_sch, audioamp.kicad_sch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]
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2025-08-13 v3.5: - swapped +/- connection of battery (as they are delivered normally) - fixing of footprints: FC68125 throws an error with a NPTH, fixed - fixed Pico W footprint, was not really possible to sold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
    [FABI_schematic.kicad_pcb, FABI_schematic.kicad_sch, lpw1.kicad_sch]
2025-08-19 Replaced RJ12 connector value (not available anymore); cleanup of iBOM, removed unused old csv/ods BOM
    [FABI_PCB_BOM.ods, FABI_schematic.csv, FABI_schematic.kicad_pcb, audioamp.kicad_sch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]
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2025-11-05 added 3d model for RJ12 & fixed .stp path for 3.5mm jacks
    [FABI_schematic.kicad_pcb]
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

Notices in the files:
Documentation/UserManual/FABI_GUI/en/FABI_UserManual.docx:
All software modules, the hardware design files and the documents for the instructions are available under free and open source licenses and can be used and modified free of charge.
